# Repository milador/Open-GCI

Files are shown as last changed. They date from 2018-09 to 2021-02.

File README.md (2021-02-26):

# Open-GCI

<p align="center">
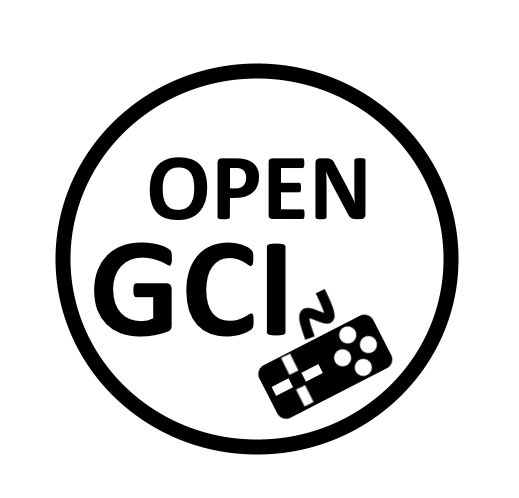
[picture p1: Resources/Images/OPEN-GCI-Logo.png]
Open-GCI Logo

</p>

An open-source accessible gaming interface that enables those with limited or no hand movement to play their favourite console based game using more accessible input methods.
Adaptive switches and USB keyboards are currently the two input methods that can be used to play console based games.

# Downloads 

These are all the files and documentation associated with the Open-GCI project.

 <table style="width:100%">
  <tr>
    <th>Resource</th>
    <th>Version</th>
    <th>Format</th>
    <th>Link</th>
  </tr>
    <tr>
    <td>Open-GCI All</td>
    <td>1.0</td>
    <td>ZIP</td>
    <td><a href="https://github.com/milador/Open-GCI/archive/master.zip">Open-GCI-master.zip</a></td>
  </tr>
  <tr>
    <td>Open-GCI Manual</td>
    <td></td>
    <td>PDF</td>
    <td></td>
  </tr>
  <tr>
    <td>Open-GCI BOM (XLSX)</td>
    <td>October 6, 2018</td>
    <td>XLSX</td>
    <td><a href="https://github.com/milador/Open-GCI/raw/master/Open-GCI_BOM.xlsx">Open-GCI_BOM.xlsx</a></td>
  </tr>
  <tr>
    <td>Open-GCI Keyboard code</td>
    <td>1.0</td>
    <td>Py</td>
    <td><a href="https://github.com/milador/Open-GCI/raw/master/Software/gci_keyboard.py">gci_keyboard.py</a></td>
  </tr>
  <tr>
    <td>Open-GCI Board Layout</td>
    <td>1.0</td>
    <td>BRD</td>
    <td><a href="https://raw.githubusercontent.com/milador/Open-GCI/master/Hardware/PCB_design/Open-GCI.brd">Open-GCI.brd</a></td>
  </tr>
  <tr>
    <td>Open-GCI Board Schematic</td>
    <td>1.0</td>
    <td>SCH</td>
    <td><a href="https://raw.githubusercontent.com/milador/Open-GCI/master/Hardware/PCB_design/Open-GCI.sch">Open-GCI.sch</a></td>
  </tr>
</table> 

# Diagram

The following diagram represents the hardware of the Open-GCI interface.

<p align="center">
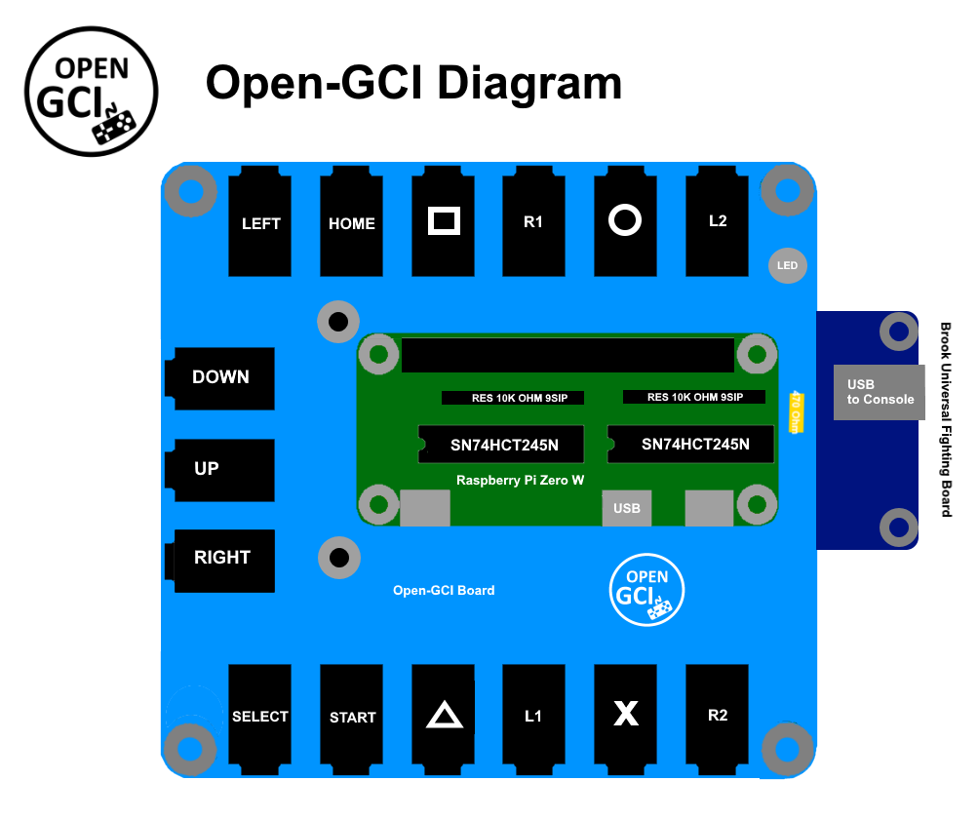
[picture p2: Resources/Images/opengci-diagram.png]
Open-GCI Diagram

</p>

# Installation 

## Hardware Setup Instructions

Coming soon..

## Software Setup Instructions

  1. Install Raspbian on an SD card according to the official documents 

https://www.raspberrypi.org/documentation/installation/installing-images/

2.	Download Dependencies

  2.1. Startup the raspberrypi zero W
  
  2.2. Open the command line
  
  2.3. Install the necessary packages
```
sudo apt-get update
sudo apt-get install build-essential python-dev python-pip git scons swig
sudo pip install RPi.GPIO
```

3.	Compile & Install rpi_ws281x Library
  
  3.1. Download the library source and compile it using following command : 
``` 
git clone https://github.com/jgarff/rpi_ws281x.git
cd rpi_ws281x
scons
``` 
  3.2. Install the Python library by executing following command : 
``` 
cd python
sudo python setup.py install
``` 
  
4.	Download gci_keyboard.py
  
  4.1. Open the command line
  
  4.2. Enter the pi directory
  
  4.3. Create a new python file using nano and name it gci_keyboard.py using following command: ```sudo nano gci_keyboar.py``` 
  
  4.4. Copy and paste the keyboard code from Software/gci_keyboard.py 
  
  4.5. Save the file and exit nano
  
5. Run code on bootup

  5.1. Open /etc/rc.local using nano by running following command: ```sudo nano /etc/rc.local```
  
  5.2. Add the following line on its own line right before exit 0: ```sudo python /home/pi/gci_keyboard.py  &```
  
  5.3. Save and exit /etc/rc.local
  
  5.4. Reboot the raspberrypi zero W by running following command: ```sudo shutdown -r now```
  
6.	Varify software is running 
  
   6.1. The Led will change color from Blue to Green when the software is ready to use

# PS4 to keyboard button mapping 

<p align="center">
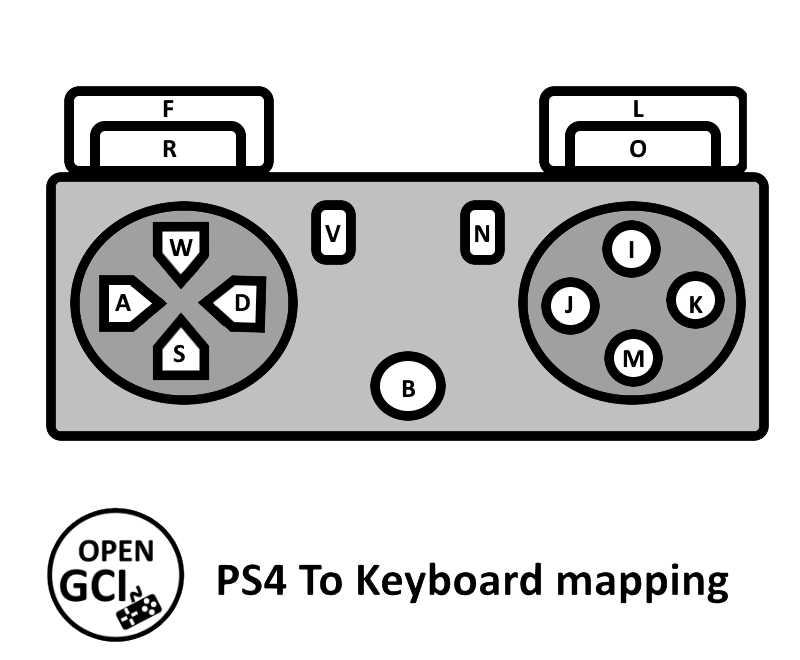
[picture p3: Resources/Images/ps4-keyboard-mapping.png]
Open-GCI PS4 to keyboard button mapping

</p>

# Picture 

<p align="center">
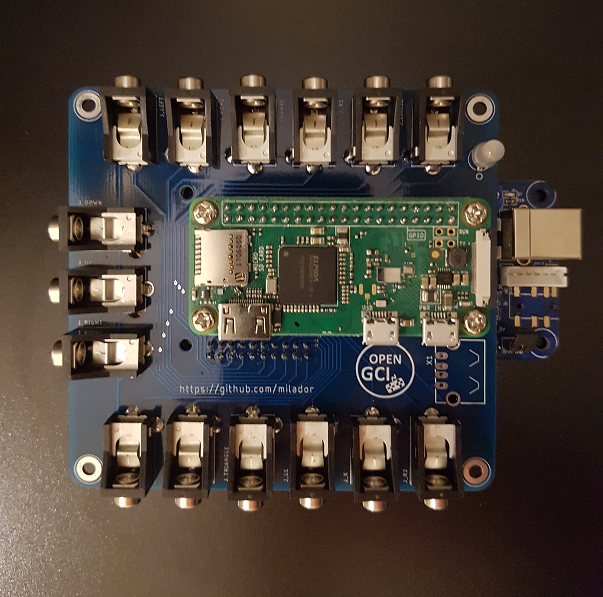
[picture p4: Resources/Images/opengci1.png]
Open-GCI Interface

</p>

# License

## Creative Commons Attribution-NonCommercial-ShareAlike (CC-BY-NC-SA)

Copyright (c) 2018 Milador

A creative commons license that bans commercial use and requires you to release any modified works under this license.

<p align="center">
CC-BY-NC-SA
</p>

<br />This work is licensed under a <a rel="license" href="http://creativecommons.org/licenses/by-nc-sa/3.0/">Creative Commons Attribution-NonCommercial-ShareAlike 3.0 Unported License</a>.

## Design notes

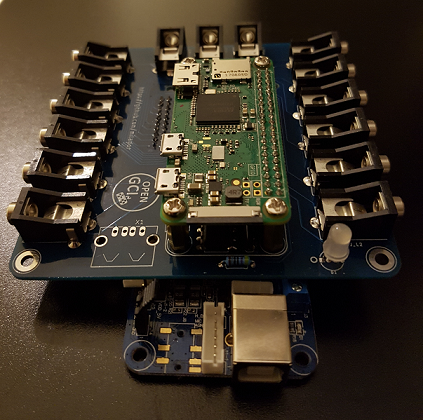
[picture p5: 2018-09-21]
Resources/Images/opengci2.png

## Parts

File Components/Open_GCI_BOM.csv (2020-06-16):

Index | Quantity | Digikey Part Number | Manufacturer Part Number | Description | Unit Price (US) | Total Price (US) | Link | Link 2
1 | 1 |  |  | RASPBERRY PI ZERO W | 10 |  | https://www.canakit.com/raspberry-pi-zero-wireless.html?src=raspberrypi
2 | 1 |  |  | Brook Universal Fighting Board | 89.95 |  | https://www.ebay.com/i/264484478017 | https://focusattack.com/brook-universal-fighting-board-with-headers/
3 | 2 | 296-1612-5-ND | SN74HCT245N | IC TXRX NON-INVERT 5.5V 20DIP | 0.6 |  | https://www.digikey.com/product-detail/en/texas-instruments/SN74HCT245N/296-1612-5-ND/277258
4 | 2 | 1568-1213-ND | COM-12986 | ADDRESS LED DISC SER RGB 5MM 5PC | 2.95 |  | https://www.digikey.com/en/products/detail/sparkfun-electronics/COM-12986/5673799
5 | 1 | S6104-ND | PPTC202LFBN-RC | CONN HEADER FEM 40POS .1" DL TIN | 2.29 |  | https://www.digikey.com/en/products/detail/sullins-connector-solutions/PPTC202LFBN-RC/807240?s=N4IgTCBcDaIApwCoGEwAYwBkBiAhAcgLQBKyIAugL5A
6 | 1 | S6106-ND | PPPC102LFBN-RC | CONN HEADER FEM 20POS.1" DL GOLD | 1.26 |  | https://www.digikey.com/en/products/detail/sullins-connector-solutions/PPPC102LFBN-RC/807245?s=N4IgTCBcDaIAoIMIEYAMYAyAxAQgOQFoAlREAXQF8g
7 | 1 | CF14JT4K70CT-ND | CF14JT4K70 | RES 470K OHM 1/4W 5% AXIAL | 0.1 |  | https://www.digikey.com/en/products/detail/stackpole-electronics-inc/CF14JT4K70/1741428?s=N4IgTCBcDaIMIDECMAWAUgFRQaQOwAYQBdAXyA
8 | 1 | 1528-1585-ND | 1099 | USB OTG HOST CABLE - MICROB OTG | 2.5 |  | https://www.digikey.com/en/products/detail/adafruit-industries-llc/1099/5875794?s=N4IgTCBcDaIIwFYwA4C0jkNQOQCIgF0BfIA
9 | 15 | CP1-3535NG-ND | SJ1-3535NG | CONN JACK STEREO 3.5MM R/A | 1.19 |  | https://www.digikey.com/en/products/detail/cui-devices/SJ1-3535NG/738699
10 | 1 |  |  | Sandisk Ultra 16GB Micro Class 10 | 6.9 |  | https://www.amazon.com/SanDisk-Ultra-Micro-Adapter-SDSQUNC-016G-GN6MA/dp/B010Q57SEE
11 | 2 | CSC10KW-ND | CSC09A0110K0GEK | RES ARRAY 8 RES 10K OHM 9SIP | 1.4 |  | https://www.digikey.com/en/products/detail/vishay-dale/CSC09A0110K0GEK/2713650?s=N4IgTCBcDaIMIGU4EYAMBpA6gWgHIBEQBdAXyA
 |  |  |  |  | Subtotal | 137.95

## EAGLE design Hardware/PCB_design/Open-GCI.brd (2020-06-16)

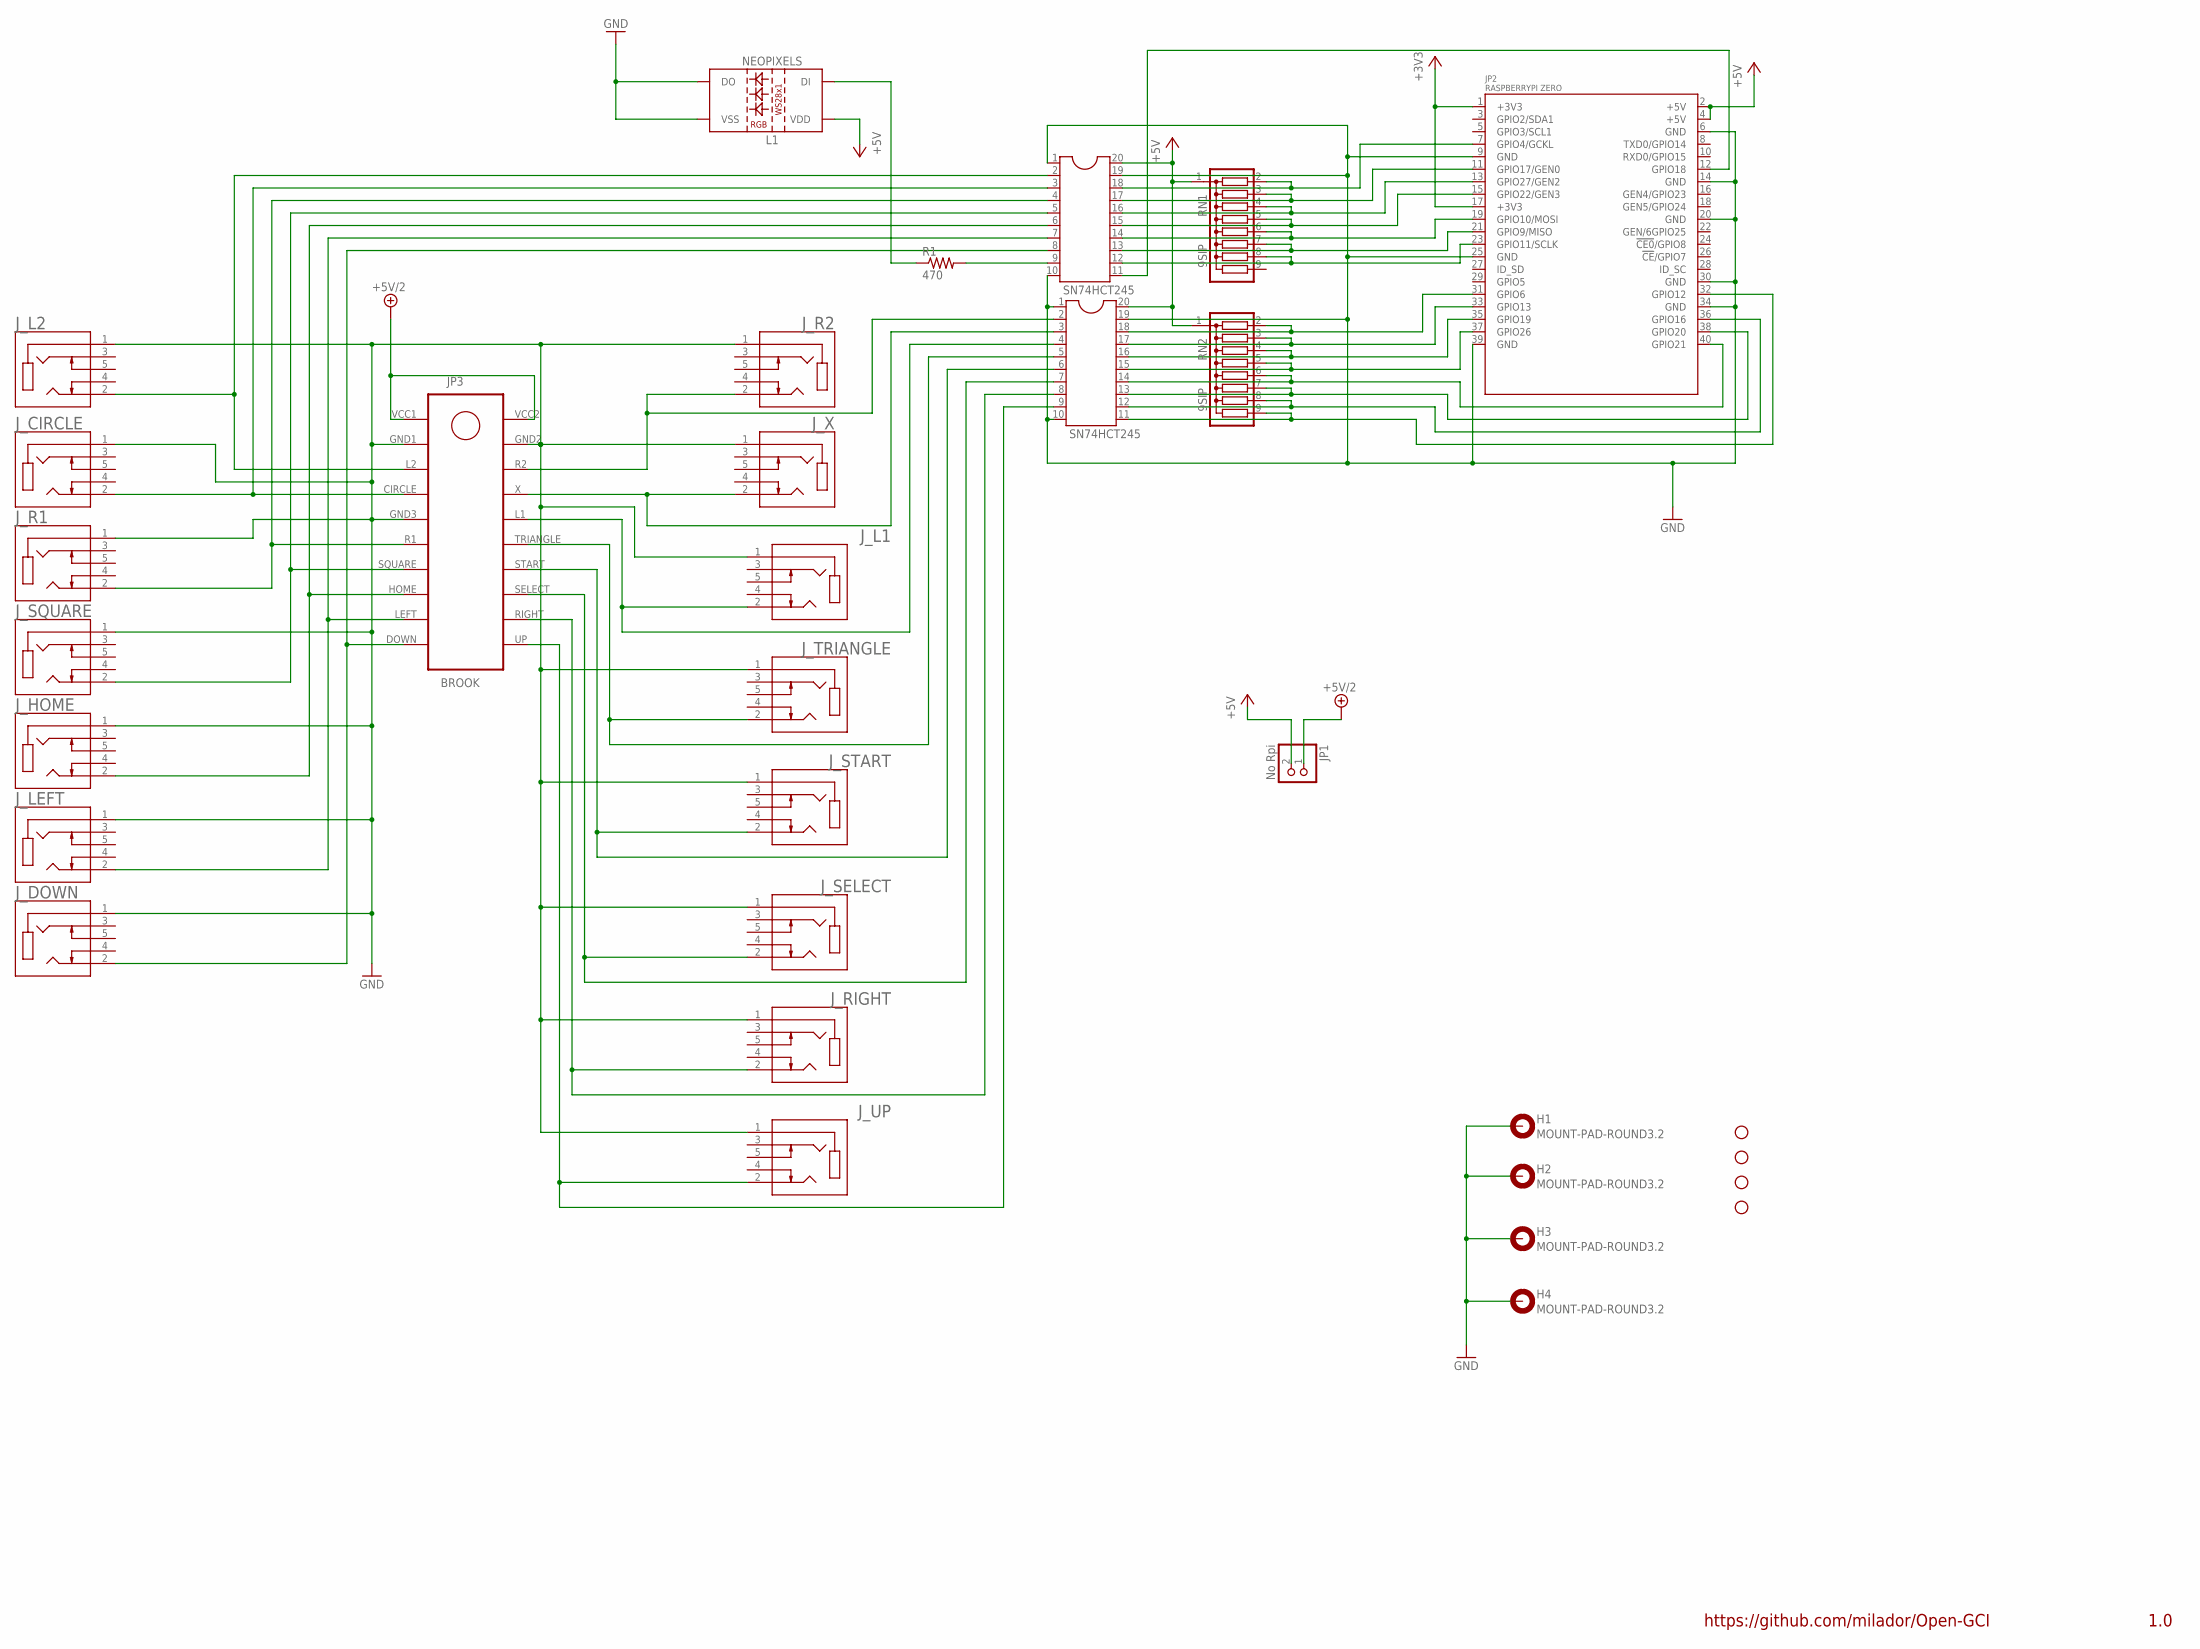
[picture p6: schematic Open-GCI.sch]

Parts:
H1, H2, H3, H4: MOUNT-PAD-ROUND3.2; 3,2-PAD
H5, H6, H7, H8: STAND-OFF
IC1, IC2: SN74HCT245
JP1: No Rpi; 1X02
JP2: RASPBERRYPI ZERO; RASPBERRYPI_ZERO
JP3: BROOK; CONN_2X10
J_CIRCLE: SJ1-3535NG; CUI_SJ1-3535NG
J_DOWN: SJ1-3535NG; CUI_SJ1-3535NG
J_HOME: SJ1-3535NG; CUI_SJ1-3535NG
J_L1, J_L2: SJ1-3535NG; CUI_SJ1-3535NG
J_LEFT: SJ1-3535NG; CUI_SJ1-3535NG
J_R1, J_R2: SJ1-3535NG; CUI_SJ1-3535NG
J_RIGHT: SJ1-3535NG; CUI_SJ1-3535NG
J_SELECT: SJ1-3535NG; CUI_SJ1-3535NG
J_SQUARE: SJ1-3535NG; CUI_SJ1-3535NG
J_START: SJ1-3535NG; CUI_SJ1-3535NG
J_TRIANGLE: SJ1-3535NG; CUI_SJ1-3535NG
J_UP: SJ1-3535NG; CUI_SJ1-3535NG
J_X: SJ1-3535NG; CUI_SJ1-3535NG
L1: NEOPIXELS; NEOPIXELS-5MM
R1: 470; 0204/7
RN1, RN2: 9SIP; SIL9

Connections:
+3V3: JP2.1 (+3V3), JP2.17 (+3V3)
+5V: IC1.20, IC2.20, JP1.2, JP2.2 (+5V), JP2.4 (+5V), L1.2 (VDD), RN1.1, RN2.1
+5V/2: JP1.1, JP3.VCC1, JP3.VCC2
GND: H1.B3,2, H2.B3,2, H3.B3,2, H4.B3,2, IC1.1, IC1.10, IC1.19, IC2.1, IC2.10, IC2.19, JP2.6 (GND), JP2.9 (GND), JP2.14 (GND), JP2.20 (GND), JP2.25 (GND), JP2.30 (GND), JP2.34 (GND), JP2.39 (GND), JP3.GND1, JP3.GND2, JP3.GND3, J_CIRCLE.1, J_DOWN.1, J_HOME.1, J_L1.1, J_L2.1, J_LEFT.1, J_R1.1, J_R2.1, J_RIGHT.1, J_SELECT.1, J_SQUARE.1, J_START.1, J_TRIANGLE.1, J_UP.1, J_X.1, L1.3 (VSS), L1.4 (DO)
unnamed: IC1.9, R1.2
unnamed: L1.1 (DI), R1.1
NGP7: IC1.18, JP2.7 (GPIO4/GCKL), RN1.2
NGP11: IC1.17, JP2.11 (GPIO17/GEN0), RN1.3
NGP12: IC1.11, JP2.12 (GPIO18)
NGP13: IC1.16, JP2.13 (GPIO27/GEN2), RN1.4
NGP15: IC1.15, JP2.15 (GPIO22/GEN3), RN1.5
NGP19: IC1.14, JP2.19 (GPIO10/MOSI), RN1.6
NGP21: IC1.13, JP2.21 (GPIO9/MISO), RN1.7
NGP23: IC1.12, JP2.23 (GPIO11/SCLK), RN1.8
NGP31: IC2.18, JP2.31 (GPIO6), RN2.2
NGP32: IC2.11, JP2.32 (GPIO12), RN2.9
NGP33: IC2.17, JP2.33 (GPIO13), RN2.3
NGP35: IC2.16, JP2.35 (GPIO19), RN2.4
NGP36: IC2.12, JP2.36 (GPIO16), RN2.8
NGP37: IC2.15, JP2.37 (GPIO26), RN2.5
NGP38: IC2.13, JP2.38 (GPIO20), RN2.7
NGP40: IC2.14, JP2.40 (GPIO21), RN2.6
NJ_CIR: IC1.3, JP3.CIRCLE, J_CIRCLE.2
NJ_DOWN: IC1.8, JP3.DOWN, J_DOWN.2
NJ_HOME: IC1.6, JP3.HOME, J_HOME.2
NJ_L1: IC2.4, JP3.L1, J_L1.2
NJ_L2: IC1.2, JP3.L2, J_L2.2
NJ_LEFT: IC1.7, JP3.LEFT, J_LEFT.2
NJ_R1: IC1.4, JP3.R1, J_R1.2
NJ_R2: IC2.2, JP3.R2, J_R2.2
NJ_RIGHT: IC2.8, JP3.RIGHT, J_RIGHT.2
NJ_SELECT: IC2.7, JP3.SELECT, J_SELECT.2
NJ_SQU: IC1.5, JP3.SQUARE, J_SQUARE.2
NJ_START: IC2.6, JP3.START, J_START.2
NJ_TRI: IC2.5, JP3.TRIANGLE, J_TRIANGLE.2
NJ_UP: IC2.9, JP3.UP, J_UP.2
NJ_X: IC2.3, JP3.X, J_X.2

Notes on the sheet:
https://github.com/milador/Open-GCI
1.0

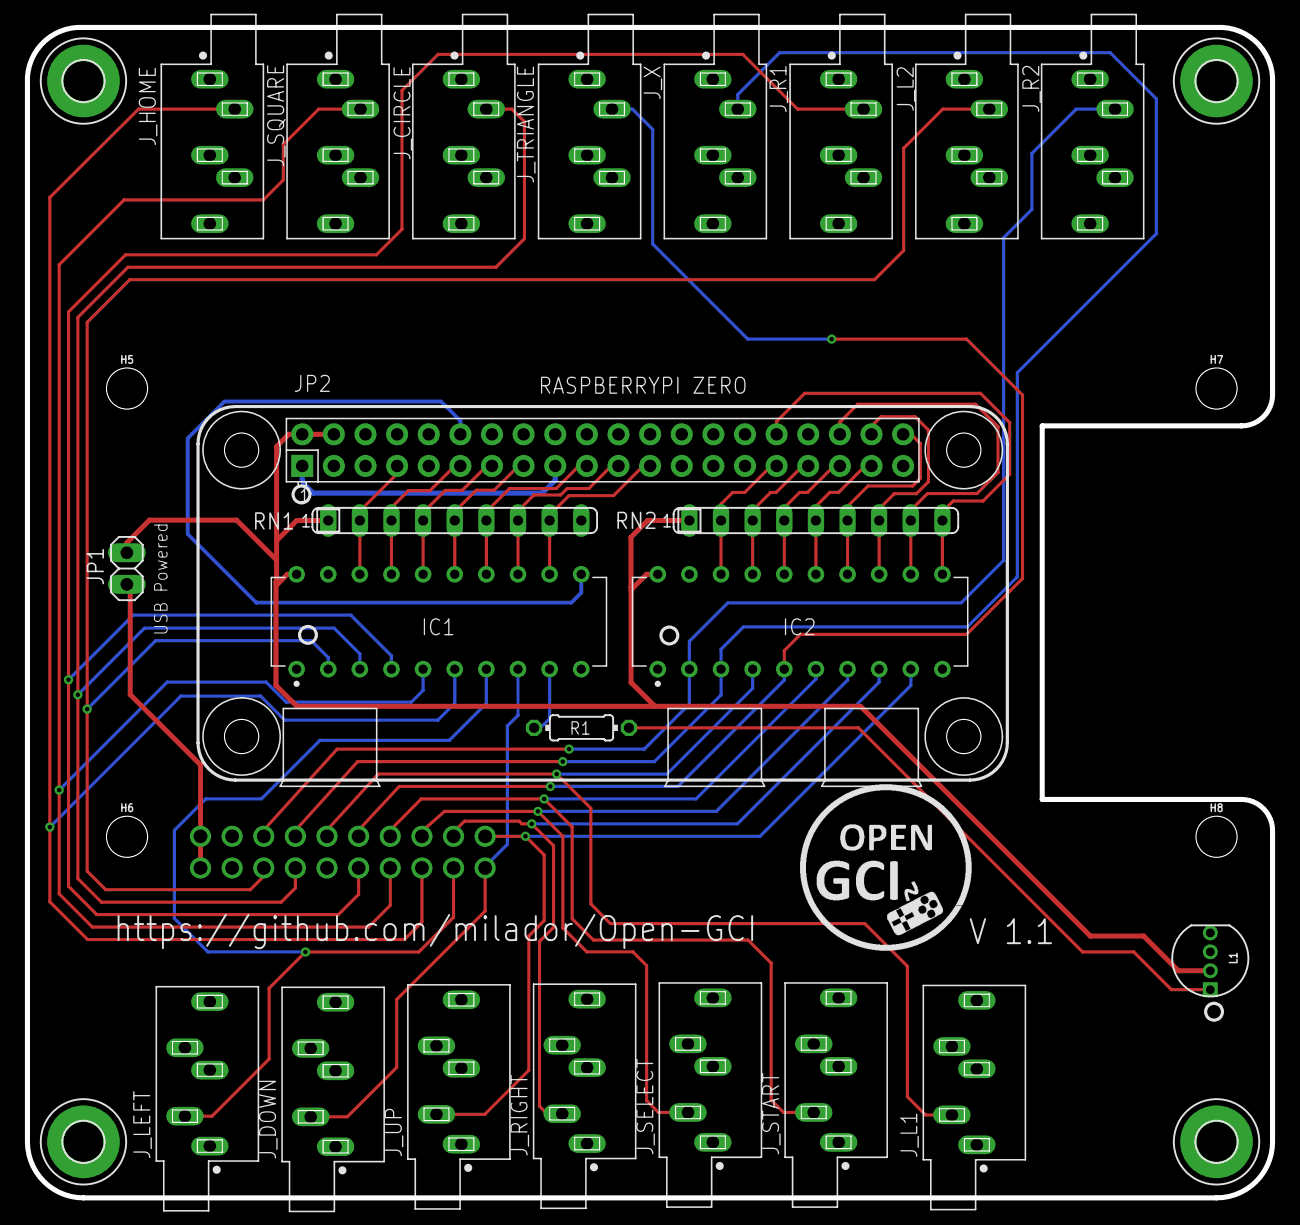
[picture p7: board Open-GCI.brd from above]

Board: 2 copper layers, 100.0 x 94.0 mm, 32 parts (1 on the bottom side), 37 nets.

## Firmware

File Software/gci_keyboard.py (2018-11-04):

# File name: gci_keyboard.py
# Author: Milad Hajihassan
# Date created: 8/10/2018
# Date last modified: 11/03/2018
# Python Version: 2.7

import os
import sys    
import termios
import fcntl
import RPi.GPIO as gpio
import time
from neopixel import *
import argparse
import random

# LED configuration:
LED_COUNT      = 1      # Number of LED pixels.
LED_PIN        = 18      # GPIO pin connected to the pixels (18 uses PWM!).
LED_FREQ_HZ    = 800000  # LED signal frequency in hertz
LED_DMA        = 10      # DMA channel to use for generating signal
LED_BRIGHTNESS = 33     # Set brightest
LED_INVERT     = False   # True to invert the signal
LED_CHANNEL    = 0       # set to '1' for GPIOs 13, 19, 41, 45 or 53

# LED cleanup:
def colorWipe(strip, color, wait_ms=50):
     strip.setPixelColor(0, color)
     strip.show()
     time.sleep(wait_ms/1000.0)

# LED startup:
def colorStartup(strip, color=Color(255, 50, 0), wait_ms=400, iterations=3):
    for i in range(iterations):
        strip.setPixelColor(0, color)
        strip.show()
        time.sleep(wait_ms/1000.0)
        strip.setPixelColor(0, Color(0,0,0))
        strip.show()
        time.sleep(wait_ms/1000.0)

		
def getch():
  import sys, tty, termios
  init()
  sleep_time = 0.050
  old_settings = termios.tcgetattr(0)
  new_settings = old_settings[:]
  new_settings[3] &= ~termios.ICANON

  try:
    colorWipe(strip, Color(0,255,0), 10)
    termios.tcsetattr(0, termios.TCSANOW, new_settings)
    ch = sys.stdin.read(1)
    if (ch == 'w'):
        action_up(sleep_time)
    elif ch == 's':
        action_down(sleep_time)
    elif ch == 'a':
        action_left(sleep_time)
    elif ch == 'd':
        action_right(sleep_time)
    elif ch == 'm':
        action_x(sleep_time)
    elif ch == 'i':
        action_triangle(sleep_time)
    elif ch == 'j':
        action_square(sleep_time)
    elif ch == 'k':
        action_o(sleep_time)
    elif ch == 'r':
        action_l1(sleep_time)
    elif ch == 'f':
        action_l2(sleep_time)
    elif ch == 'o':
        action_r1(sleep_time)
    elif ch == 'l':
        action_r2(sleep_time)
    elif ch == 'v':
        action_select(sleep_time)
    elif ch == 'b':
        action_home(sleep_time)
    elif ch == 'n':
        action_start(sleep_time)
    elif ch == 'q':
        clean_up() 
        sys.exit()
    else:
        clean_up()
        pass
    init()
      
  finally:
    termios.tcsetattr(0, termios.TCSANOW, old_settings)
  return ch

# Initialization 
def init():
    gpio.setmode(gpio.BOARD)
    gpio.setup(7, gpio.OUT)
    gpio.setup(11, gpio.OUT)
    gpio.setup(13, gpio.OUT)
    gpio.setup(15, gpio.OUT)
    gpio.setup(19, gpio.OUT)
    gpio.setup(21, gpio.OUT)
    gpio.setup(23, gpio.OUT)
    gpio.setup(31, gpio.OUT)
    gpio.setup(32, gpio.OUT) 
    gpio.setup(33, gpio.OUT)
    gpio.setup(35, gpio.OUT)
    gpio.setup(36, gpio.OUT)
    gpio.setup(37, gpio.OUT)
    gpio.setup(38, gpio.OUT)
    gpio.setup(40, gpio.OUT)

def action_l2(tf):
    gpio.output(7, False)
    gpio.output(11, True)
    gpio.output(13, True)
    gpio.output(15, True)
    gpio.output(19, True)
    gpio.output(21, True)
    gpio.output(23, True)
    gpio.output(31, True)
    gpio.output(32, True) 
    gpio.output(33, True)
    gpio.output(35, True)
    gpio.output(36, True)
    gpio.output(37, True)
    gpio.output(38, True)
    gpio.output(40, True)

def action_o(tf):
    gpio.output(7, True)
    gpio.output(11, False)
    gpio.output(13, True)
    gpio.output(15, True)
    gpio.output(19, True)
    gpio.output(21, True)
    gpio.output(23, True)
    gpio.output(31, True)
    gpio.output(32, True) 
    gpio.output(33, True)
    gpio.output(35, True)
    gpio.output(36, True)
    gpio.output(37, True)
    gpio.output(38, True)
    gpio.output(40, True)
	
def action_r1(tf):
    gpio.output(7, True)
    gpio.output(11, True)
    gpio.output(13, False)
    gpio.output(15, True)
    gpio.output(19, True)
    gpio.output(21, True)
    gpio.output(23, True)
    gpio.output(31, True)
    gpio.output(32, True) 
    gpio.output(33, True)
    gpio.output(35, True)
    gpio.output(36, True)
    gpio.output(37, True)
    gpio.output(38, True)
    gpio.output(40, True)
	
def action_square(tf):
    gpio.output(7, True)
    gpio.output(11, True)
    gpio.output(13, True)
    gpio.output(15, False)
    gpio.output(19, True)
    gpio.output(21, True)
    gpio.output(23, True)
    gpio.output(31, True)
    gpio.output(32, True) 
    gpio.output(33, True)
    gpio.output(35, True)
    gpio.output(36, True)
    gpio.output(37, True)
    gpio.output(38, True)
    gpio.output(40, True)
	
def action_home(tf):
    gpio.output(7, True)
    gpio.output(11, True)
    gpio.output(13, True)
    gpio.output(15, True)
    gpio.output(19, False)
    gpio.output(21, True)
    gpio.output(23, True)
    gpio.output(31, True)
    gpio.output(32, True) 
    gpio.output(33, True)
    gpio.output(35, True)
    gpio.output(36, True)
    gpio.output(37, True)
    gpio.output(38, True)
    gpio.output(40, True)
	
def action_left(tf):
    gpio.output(7, True)
    gpio.output(11, True)
    gpio.output(13, True)
    gpio.output(15, True)
    gpio.output(19, True)
    gpio.output(21, False)
    gpio.output(23, True)
    gpio.output(31, True)
    gpio.output(32, True) 
    gpio.output(33, True)
    gpio.output(35, True)
    gpio.output(36, True)
    gpio.output(37, True)
    gpio.output(38, True)
    gpio.output(40, True)
	
def action_down(tf):
    gpio.output(7, True)
    gpio.output(11, True)
    gpio.output(13, True)
    gpio.output(15, True)
    gpio.output(19, True)
    gpio.output(21, True)
    gpio.output(23, False)
    gpio.output(31, True)
    gpio.output(32, True) 
    gpio.output(33, True)
    gpio.output(35, True)
    gpio.output(36, True)
    gpio.output(37, True)
    gpio.output(38, True)
    gpio.output(40, True)
	
	
def action_r2(tf):
    gpio.output(7, True)
    gpio.output(11, True)
    gpio.output(13, True)
    gpio.output(15, True)
    gpio.output(19, True)
    gpio.output(21, True)
    gpio.output(23, True)
    gpio.output(31, False)
    gpio.output(32, True) 
    gpio.output(33, True)
    gpio.output(35, True)
    gpio.output(36, True)
    gpio.output(37, True)
    gpio.output(38, True)
    gpio.output(40, True)
	
def action_x(tf):
    gpio.output(7, True)
    gpio.output(11, True)
    gpio.output(13, True)
    gpio.output(15, True)
    gpio.output(19, True)
    gpio.output(21, True)
    gpio.output(23, True)
    gpio.output(31, True)
    gpio.output(32, True) 
    gpio.output(33, False)
    gpio.output(35, True)
    gpio.output(36, True)
    gpio.output(37, True)
    gpio.output(38, True)
    gpio.output(40, True)
	
def action_l1(tf):
    gpio.output(7, True)
    gpio.output(11, True)
    gpio.output(13, True)
    gpio.output(15, True)
    gpio.output(19, True)
    gpio.output(21, True)
    gpio.output(23, True)
    gpio.output(31, True)
    gpio.output(32, True) 
    gpio.output(33, True)
    gpio.output(35, False)
    gpio.output(36, True)
    gpio.output(37, True)
    gpio.output(38, True)
    gpio.output(40, True)

def action_triangle(tf):
    gpio.output(7, True)
    gpio.output(11, True)
    gpio.output(13, True)
    gpio.output(15, True)
    gpio.output(19, True)
    gpio.output(21, True)
    gpio.output(23, True)
    gpio.output(31, True)
    gpio.output(32, True) 
    gpio.output(33, True)
    gpio.output(35, True)
    gpio.output(36, True)
    gpio.output(37, False)
    gpio.output(38, True)
    gpio.output(40, True)

def action_start(tf):
    gpio.output(7, True)
    gpio.output(11, True)
    gpio.output(13, True)
    gpio.output(15, True)
    gpio.output(19, True)
    gpio.output(21, True)
    gpio.output(23, True)
    gpio.output(31, True)
    gpio.output(32, True) 
    gpio.output(33, True)
    gpio.output(35, True)
    gpio.output(36, True)
    gpio.output(37, True)
    gpio.output(38, True)
    gpio.output(40, False)

def action_select(tf):
    gpio.output(7, True)
    gpio.output(11, True)
    gpio.output(13, True)
    gpio.output(15, True)
    gpio.output(19, True)
    gpio.output(21, True)
    gpio.output(23, True)
    gpio.output(31, True)
    gpio.output(32, True) 
    gpio.output(33, True)
    gpio.output(35, True)
    gpio.output(36, True)
    gpio.output(37, True)
    gpio.output(38, False)
    gpio.output(40, True)

def action_right(tf):
    gpio.output(7, True)
    gpio.output(11, True)
    gpio.output(13, True)
    gpio.output(15, True)
    gpio.output(19, True)
    gpio.output(21, True)
    gpio.output(23, True)
    gpio.output(31, True)
    gpio.output(32, True) 
    gpio.output(33, True)
    gpio.output(35, True)
    gpio.output(36, False)
    gpio.output(37, True)
    gpio.output(38, True)
    gpio.output(40, True)
	
def action_up(tf):
    gpio.output(7, True)
    gpio.output(11, True)
    gpio.output(13, True)
    gpio.output(15, True)
    gpio.output(19, True)
    gpio.output(21, True)
    gpio.output(23, True)
    gpio.output(31, True)
    gpio.output(32, False) 
    gpio.output(33, True)
    gpio.output(35, True)
    gpio.output(36, True)
    gpio.output(37, True)
    gpio.output(38, True)
    gpio.output(40, True)
	
def clean_up():
    gpio.output(7, True)
    gpio.output(11, True)
    gpio.output(13, True)
    gpio.output(15, True)
    gpio.output(19, True)
    gpio.output(21, True)
    gpio.output(23, True)
    gpio.output(31, True)
    gpio.output(32, True) 
    gpio.output(33, True)
    gpio.output(35, True)
    gpio.output(36, True)
    gpio.output(37, True)
    gpio.output(38, True)
    gpio.output(40, True)
    colorWipe(strip, Color(0,0,0), 10)
    gpio.cleanup()   


def main():
  
  while True:
        print("\nKey: '" + getch() + "'\n")
      



if __name__ == "__main__":
    # Create NeoPixel object with appropriate configuration.
    strip = Adafruit_NeoPixel(LED_COUNT, LED_PIN, LED_FREQ_HZ, LED_DMA, LED_INVERT, LED_BRIGHTNESS, LED_CHANNEL)
    # Intialize the library 
    strip.begin()
    colorStartup(strip)
    colorWipe(strip, Color(0,255,0), 10)
    main()

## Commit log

2018-10-07 Added part list and the PCB file
    [Open-GCI.brd, Open-GCI.sch, Open-GCI_BOM.xlsx]
2018-10-07 Updated the schematics
    [Open-GCI.sch]
2018-10-21 Fixed the 3.5mm jack issue
    [Open-GCI.brd, Open-GCI.sch]
2020-06-16 Updated PCB, Component listand gerber files
    [Open-GCI.brd, Open-GCI.sch, Open-GCI_BOM.xlsx, Open_GCI_BOM.csv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]

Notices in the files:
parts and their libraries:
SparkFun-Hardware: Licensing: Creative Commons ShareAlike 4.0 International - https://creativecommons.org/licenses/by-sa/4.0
